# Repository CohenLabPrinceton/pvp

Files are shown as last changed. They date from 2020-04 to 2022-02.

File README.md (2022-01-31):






# The People's Ventilator Project

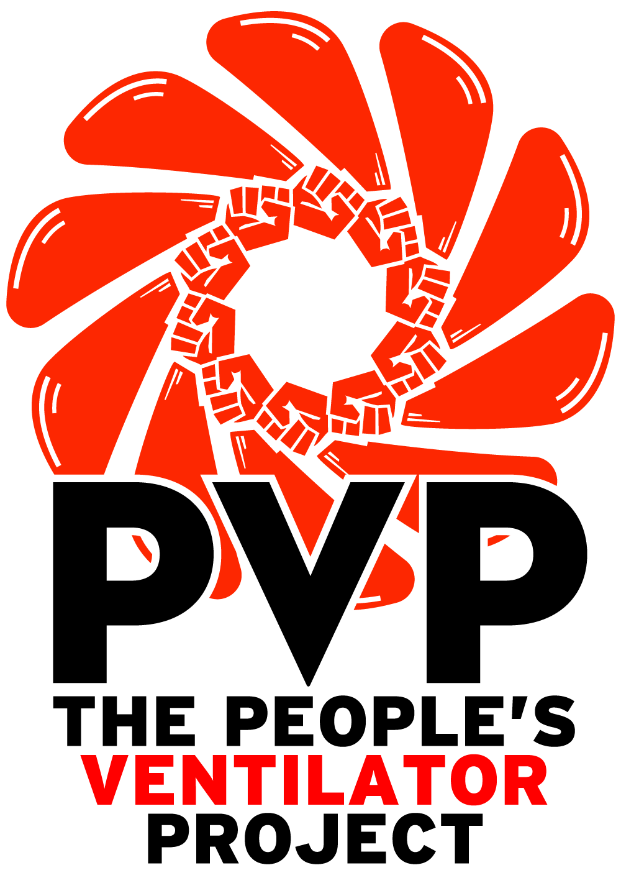
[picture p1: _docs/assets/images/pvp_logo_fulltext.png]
PVP Logo


All information is in the documentation:
https://pvp.readthedocs.io/

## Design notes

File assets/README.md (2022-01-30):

# Content of assets
This folder contains all technical drawings for PVP1, the drawings for parts to be 3D-printed, and printed circuit boards.
In addition, to aid discoverability, we have generated a standardized Open Know How Manifest (OKH-manifest): [`okh-manifest.yml`](okh-manifest.yml). This follows the Open Know-How Manifest Specification Version 1.0. Finally, the file `PVP1 Assembly Instructions.pdf` contains detailed step-by-step assembly instructions.
The following folders exist:

# cad
Contains a 3D-printable PEEP valve, as single-use PEEP valves can be subject to supply chain limitations. 

# DXFs
Contains drawings for laser cutting of the chassis.

# PCBS
This folder contains all of the electrical design files for our custom PCBs. 

# SOLIDWORKS
This folder contains CAD drawings of PVP1, more specifically:
1. Technical drawings of the PVP1 Mk3, in Solidworks. This is the device documented in the article, and featured in the detailed assembly instructions. This final version of PVP1 removed non-critical components, such as the humidifier and Gauges, and introduced more standardized parts.
1. The previous version of the device, Mk2, using few standardized components, and featuring a humidifier. Notice the `CPAP_BIPAP_HEATER_HUMIDIFIER_ASSY`.
1. Mk1, the first version of PVP1. This served as an early sketch about what to include in the design

# STLs
This folder contains all of our 3D printed components/fixtures that are not included in our Bill-of-Materials.

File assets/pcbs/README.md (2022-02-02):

# Content of pcbs
This folder contains PCB design files for the PVP1. There are two boards: one for the Actuators and one for the Sensors. They connect to the the Raspberry Pi 4 via 40-pin stackable headers. Uploaded as KiCad project files except where noted.

# Actuator Board (actuators-rev2)
	- Interfaces the Raspberry Pi to the inspiratory and expiratory valves through an array of solenoid drivers (ULN2003A Darlington transistor array)
	- Revision history:
		- rev2 (6/14/2020): Present version. Removed one screw terminal and the adjustable headers. Four of the darlington pairs are tied together to drive the expiratory valve, and three are tied together to drive the proportional valve. These connections are now permanent traces on the PCB.
		- rev1 (5/13/2020): Initial version. Three screw terminals intended to connect to valves. Included extra jumpers J4, J8, J9, and J10 designed to tie together Darlington pairs for felxibility if more current was needed to drive a particular valve.
		
# Sensor Board (pressure-rev2)
	- Interfaces four analog output sensors with the Raspberry Pi via I^2C commands to a 12-bit 4-channel ADC (Adafruit ADS1015)
	- Revision history:
		- rev2 (6/14/2020): Present version. Added a third auxiliary pressure sensor, and revised analog front-end for oxygen sensor. Added a TL7660 charge pump to provide a dual-sided supply to the INA126 instrumentation amplifier. Connections for I2C resistors removed.
		- rev1 (4/27/2020): Initial version. Shared as Gerber production files. Connections included for two pressure sensors, oxygen sensor, and flow sensor.

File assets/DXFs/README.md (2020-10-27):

This folder contains the .DXF files for the HDPE side panels, primarily for laser cutting applications. 

Produce two copies of the "SIDE_IP_PANEL", and one of each of the rest!

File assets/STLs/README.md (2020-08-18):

This folder contains the STL files for 3D printed adapters and brackets.

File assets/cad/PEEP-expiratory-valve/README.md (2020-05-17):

This folder contains CAD files (including Solidworks assembly and part files, STLs, and STEP versions) of the PEEP valve components.

This hardware design is licensed under the CERN Open Hardware Licence v1.2 (CERN, Geneva, Switzerland). Refer to the text file cern_ohl_v_1_2 or https://ohwr.org/project/licenses/wikis/cern-ohl-v1.2 for details. 

In the event that a commercial PEEP valve cannot be sourced, we provide these 3D printable components so that a user can produce a DIY PEEP version of the valve.

This part may serve either as a traditional PEEP valve in its standard configuration, or as a combined expiratory valve + PEEP valve, by tapping the hole in the cap with a 1/4" NPT tap, and applying pressure to this port. 

We 3D printed the PEEP valve using both ABS and PLA, on a FlashForge and Creality Ender 3 printer, respectively. 

If you are printing the PEEP components, we recommend the following print settings:

- Print at triple vertical shell and 4 horizontal shell. 
- Minimum 40% infill. (We printed ours at 20% in ABS and everything seals well, but higher infill is recommended with PLA).

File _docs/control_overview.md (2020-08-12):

# pvp control pseudocode
Describes the procedure to operate low-cost ventilator under pressure control

## Pressure control parameters
**Set in GUI**
- PIP: peak inhalation pressure (~20 cm H2O)
- T_insp: inspiratory time to PEEP (~0.5 sec)
- I/E: inspiratory to expiratory time ratio
- bpm: breaths per minute (15 bpm -> 1/15 sec cycle time)
- PIP_time: Target time for PIP. While lungs expand, dP/dt should be PIP/PIP_time
- flow_insp: nominal flow rate during inspiration

**Set by hardware**
- FiO2: fraction of inspired oxygen, set by blender
- max_flow: manual valve at output of blender
- PEEP: positive end-expiratory pressure, set by manual valve

**Derived parameters**
- cycle_time: 1/bpm
- t_insp: inspiratory time, controlled by cycle_time and I/E
- t_exp: expiratory time, controlled by cycle_time and I/E

**Monitored variables**
- Tidal volume: the volume of air entering the lung, derived from flow through t_exp
- PIP: peak inspiratory pressure, set by user in software
- Mean plateau pressure: derived from pressure sensor during inspiration cycle hold (no flow)
- PEEP: positive end-expiratory pressure, set by manual valve

**Alarms**
- Oxygen out of range
- High pressure (tube/airway occlusion)
- Low-pressure (disconnect)
- Temperature out of range 
- Low voltage alarm (if using battery power)
- Tidal volume (expiratory) out of range

## Hardware
**Sensors**
- O2 fraction, in inspiratory path
- Pressure, just before wye to endotrachial tube
- Flow, on expiratory path
- Temperature
- Humidity?

**Actuators**
- Inspiratory valve
    - Proportional or on/off
    - Must maintain low flow during expiratory cycle to maintain PEEP
- Expiratory valve
    - On/off in conjunction with PEEP valve probably OK

## Pressure control loop
1. Begin inhalation
    - v1 Triggered by program every 1/bpm sec
    - v2 triggered by momentary drop in pressure when patient initiates inhalation (technically pressure-assisted control, PAC)
    1. ExpValve.close()
    2. InspValve.set(flow_insp)
2. While PSensor.read() < PIP
    1. Monitor d(PSensor.read())/dt
    2. Adjust flow rate for desired slope with controller
4. Cut flow and hold for t_insp
    1. InspValve.close()
    2. Monitor PSensor.read() and average across this time interval to report mean plateau pressure
5. Begin exhalation and hold for t_exp
    1. InspValve.set(PEEP_flow_rate) (alt: switch to parallel tube with continuous flow)
    2. ExpValve.open()
    3. integrate(FSensor.read()) for t_exhalation to determine V_tidal
6. Repeat from step 1.

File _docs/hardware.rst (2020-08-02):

Hardware
=========

Mechanical Diagram
----------------

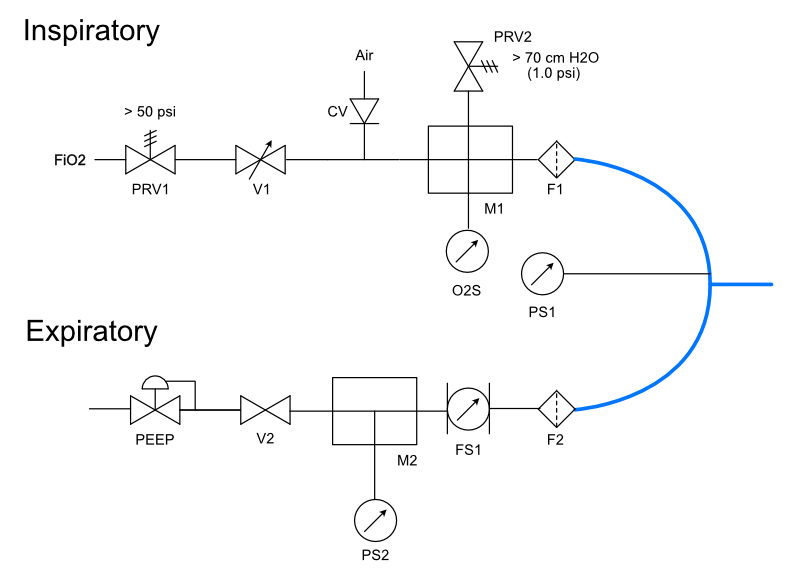
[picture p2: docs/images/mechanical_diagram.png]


    Schematic diagram of main mechanical components

.. toctree::
   :maxdepth: 4
   :caption: Hardware:

   Flow Actuators <hardware.actuators>
   Sensors <hardware.sensors>
   Safety Components <hardware.safety>
   Tubing and adapters <hardware.tubing>
   
Flow actuators
-------------------    
- Actuator PCB/overview (link to PCB with BoM, schematic, layout, etc.)    
- Proportional solenoid valve (V1) (link to doc with crit specs, driving circuit, part spec, datasheet, alternatives, etc.)
- Expiratory valve (V2) (link to doc with crit specs, driving circuit, part spec, datasheet, etc.)
    
Sensors
-------------------
- Sensor PCB/overview (link to PCB with BoM, schematic, layout, etc.)
- Oxygen sensor (O2S) (link to doc with crit specs, interface circuit, part spec, datasheet, alternatives, etc.)
- Proximal pressure sensor (PS1)
- Expiratory pressure sensor (PS2)
- Expiratory flow sensor (FS1)

Safety Components
-------------------
- 50 psi, high pressure relief valve (PRV1)
- Safety check valve (CV)
- 70 cmH2O patient-side pressure relief valve (PRV2)
- Filters (F1, F2)
- PEEP valve (PEEP) (include the design bifurcation in this module description)

Tubing and Adapters
-------------------
- Manifold 1
- Manifold 2
- Mounting Bracket 1... etc.

Bill of Materials (need to think about what goes in this table, probably separate BoMs into tables by category, but here's a sample table)
-------------------

.. list-table:: 
   :widths: 15 50 50 50
   :header-rows: 1

   * - Ref
     - Name
     - Part
     - Description
   * - V1
     - Inspiratory on/off valve
     - red hat process valve
     - completely cut off flow if required
   * - PRV1
     - High pressure relief valve
     - Sets to 50 psi
     - regulates upstream pressure to 50 psi
   * - CV
     - Inspiratory check valve
     - valve stat here
     - In case of emergency power loss, allows patient to continue taking breaths from air
   * - PRV2
     - Maximum pressure valve
     - ...
     - Sets absolute maximum pressure at patient side to 53 cm H2O
   * - F1/F2
     - Filters
     - HEPA filters?
     - Keeps the system's sensors from becoming contaminated
   * - O2S
     - Oxygen sensor
     - Sensiron ...
     - Checks FiO2 level
   * - PS1/PS2
     - Pressure sensors
     - mini4v
     - Uses gas takeoffs to measure pressure at each desired point
   * - FS1
     - Flow sensor
     - Sensiron flow sensor
     - Measures expiratory flow to calculate tidal volume
   * - M1/M2
     - Manifolds
     - 3D printed parts
     - Hubs to connect multiple components in one place
   * - V3
     - Expiratory on/off valve
     - Festo Electrical Air Directional Control Valve, 3/2 flow, Normally Closed, 8 mm Push-to-Connect
     - Opens to initiation the expiratory cycle
   * - PEEP
     - PEEP backpressure valve
     - PEEP valve
     - Sets PEEP on expiratory cycle!

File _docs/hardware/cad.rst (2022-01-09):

CAD
====

3D Printed Parts
------------------------

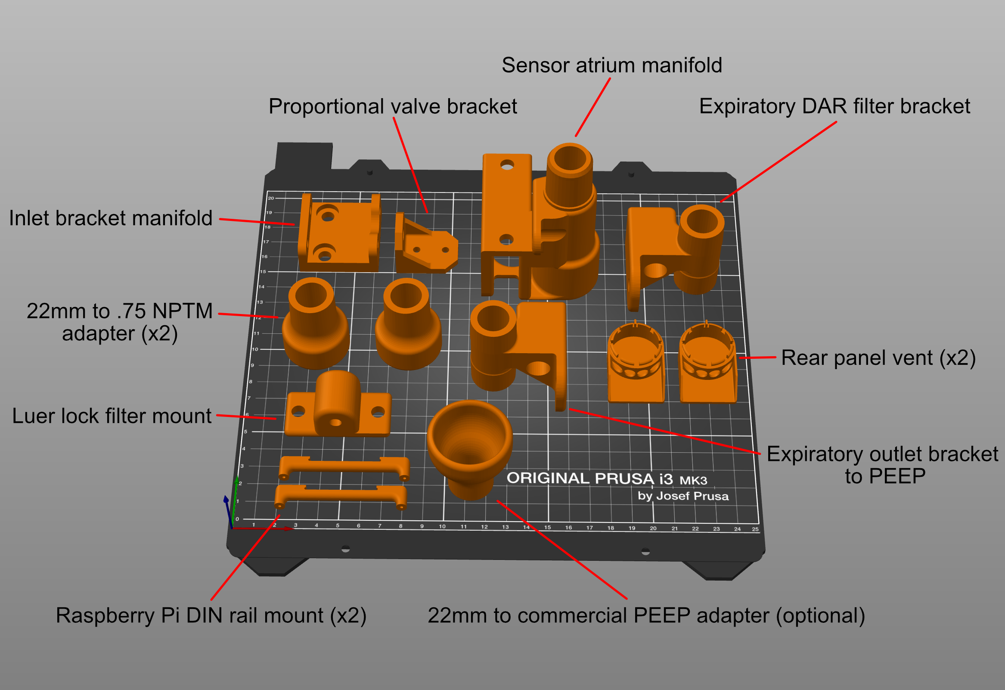
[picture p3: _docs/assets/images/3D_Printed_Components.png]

    
    Sample Prusa project with 3D printed components

Individual 3D printed parts may be downloaded here: 

* :download:`Inlet manifold bracket - [.stl] </assets/STLs/INLET_AIR_MAINFOLD_BRACKET_REV_2.STL>`
* :download:`Proportional valve bracket - [.stl] </assets/STLs/INSPIRATORY_PROPORTIONAL_VALVE_BRACKET.STL>`
* :download:`Sensor atrium manifold - [.stl] </assets/STLs/SENSOR_ATRIUM_V4.STL>`
* :download:`Expiratory DAR filter bracket - [.stl] </assets/STLs/EXPIRATORY_DAR_FILTER_BRACKET.STL>`
* :download:`22mm to 0.75 NPTM adapter (x2) - [.stl] </assets/STLs/22MM_OD_TO_0.75_NPTM_ADAPTER.STL>`
* :download:`Expiratory outlet bracket to PEEP - [.stl] </assets/STLs/EXPIRATORY_OUTLET_BRACKET_TO_PEEP_DVC.STL>`
* :download:`Luer lock filter mount - [.stl] </assets/STLs/LUER_LOCK_FILTER_MOUNT_V1.STL>`
* :download:`Raspberry Pi DIN rail mount (x2) - [.stl] </assets/STLs/RASP_PI_DIN_RAIL_MOUNT_v3.STL>`
* :download:`Rear panel vent (x2) - [.stl] </assets/STLs/IP_PANEL_VENT.STL>`
* :download:`22mm to commercial PEEP adapter - [.stl] </assets/STLs/22MM_OD_TO_COMMERCIAL_PEEP_ADAPTER.STL>`

Optional RPi DIN rail mount alternative, if your printer cannot handle the feature resolution on the original DIN rail mount: 

* :download:`ALTERNATIVE Raspberry Pi DIN rail mount (x2) - [.stl] <../assets/STLs/Alternative_Raspberry_Pi_DIN_Rail_Clip.stl>`

Download all parts:

* :download:`All components - [.zip] <../assets/STLs/All_STLs.zip>`

Printing tips: Be sure to maintain high infill for airway components: ideally, use 4 wall-layers (vertical layers), minimum 40% infill, and 4 layers on both the top and bottom. Parts should be leak-tested prior to installation, for instance, with a stopper and water bath. Most of our test prints were performed using PLA, and without any supports or rafts, since these are challenging to remove later. Supports should not be necessary provided the parts are oriented mindfully on the build plate. Also, try to keep cylindrical components oriented vertically (so that the circle is traced on the build plate); this will improve circularity of the chamber. 

For PRUSA users, we provide an example project, demonstrating part orientation:

* :download:`Sample Prusa project - [.3mf] <../assets/STLs/All_PVP1_Components.3mf>`

Enclosure
------------------------

The side, top, and bottom panels are made out of 1/16" HPDE sheeting. Laser cut, or cut by hand, two of the "SIDE_IP_PANEL", and one of each of the rest! We use a perforated HPDE for the bottom panel only; the rest are solid HPDE. 

* :download:`Bottom panel (perforated) - [.dxf] <../assets/DXFs/BOTTOM_PERFORATED_PANEL.DXF>`
* :download:`Front panel - [.dxf] <../assets/DXFs/FRONT_IP_PANEL_V1.DXF>`
* :download:`Rear panel - [.dxf] <../assets/DXFs/REAR_IP_PANEL_V1.DXF>`
* :download:`Side panel (x2) - [.dxf] <../assets/DXFs/SIDE_IP_PANEL.DXF>`
* :download:`Top panel - [.dxf] <../assets/DXFs/TOP_IP_PANEL.DXF>`

Download all .DXF files: 

* :download:`All DXF files - [.zip] <../assets/DXFs/All_DXFs.zip>`

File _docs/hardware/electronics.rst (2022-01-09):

Electronics
=============

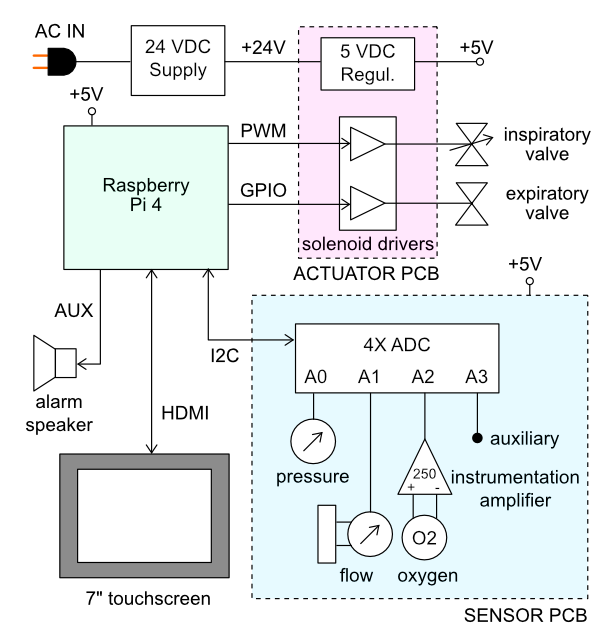
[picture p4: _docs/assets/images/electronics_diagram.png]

    
    PVP block diagram for main electrical components

The PVP is coordinated by a Raspberry Pi 4 board, which runs the graphical user interface, administers the alarm system, monitors sensor values, and sends actuation commands to the valves.
The core electrical system consists of two modular PCB 'hats', a sensor PCB and an actuator PCB, that stack onto the Raspberry Pi via 40-pin stackable headers.
The modularity of this system enables individual boards to be revised or modified to adapt to component substitutions if required.

We outsourced our PCB fabrication to Advanced Circuits, based out of Aurora, CO (for $33 each): https://www.4pcb.com/pcb-prototype-2-4-layer-boards-specials.html
If you would like to do the same, you can send them the Gerber .zip files we have provided directly.

Power and I/O
----------------
The main power to the systems is supplied by a DIN rail-mounted 150W 24V supply, which drives the inspiratory valve (4W) and expiratory valves (13W). This voltage is converted to 5V by a switched mode PCB-mounted regulated to power the Raspberry Pi and sensors.
This power is transmitted across the PCBs through the stacked headers when required.

.. csv-table:: Power and I/O bill of materials
   :file: /assets/csv/powerio_bom.csv
   :widths: 40,60
   :header-rows: 1

Sensor PCB
----------------
The sensor board interfaces four analog output sensors with the Raspberry Pi via I2C commands to a 12-bit 4-channel ADC (Adafruit ADS1015).

1. an airway pressure sensor (Amphenol 1 PSI-D-4V-MINI)
2. a differential pressure sensor (Amphenol 5 INCH-D2-P4V-MINI) to report the expiratory flow rate through a D-Lite spirometer
3. an oxygen sensor (Sensiron SS-12A) whose 13 mV differential output signal is amplified 250-fold by an instrumentation amplifier (Texas Instruments INA126)
4. a fourth auxiliary slot for an additional analog output sensor (unused)

A set of additional header pins allows for digital output sensors (such as the Sensiron SFM3300 flow sensor) to be interfaced with the Pi directly via I2C if desired. 

* :download:`Sensor PCB - [KiCad project .zip] <../assets/pcbs/pressure-rev2.zip>`

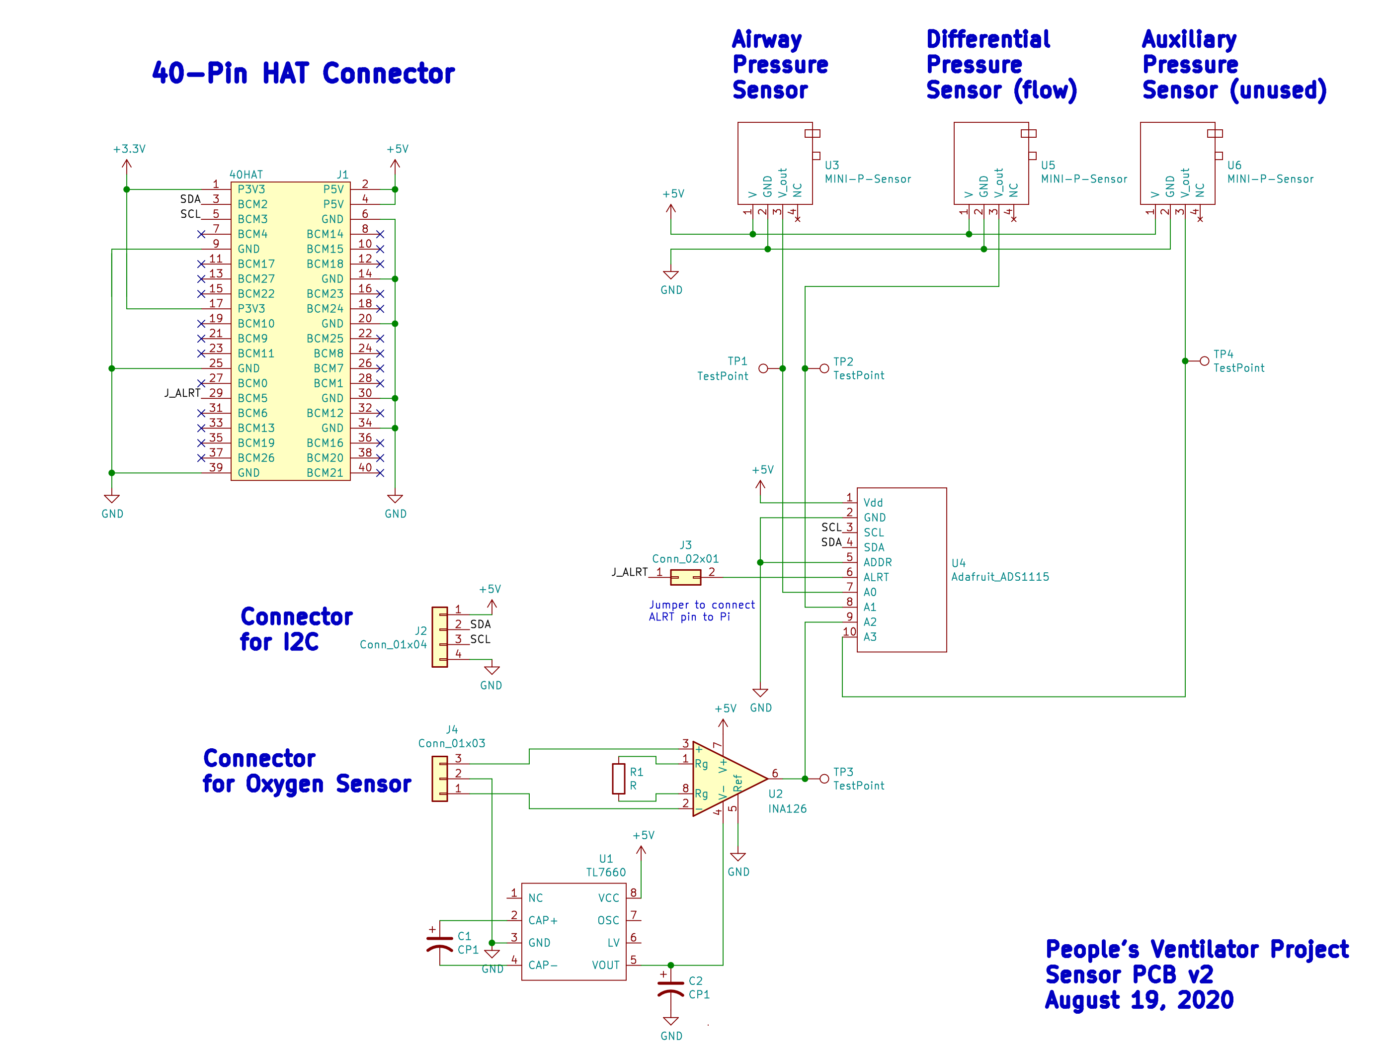
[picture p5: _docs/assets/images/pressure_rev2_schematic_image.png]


    Sensor PCB schematic
	
.. csv-table:: Sensor PCB bill of materials
   :file: /assets/csv/sensor_pcb_bom.csv
   :widths: 10,30,60
   :header-rows: 1

Actuator PCB
----------------
The purpose of the actuator board is twofold:

1. regulate the 24V power supply to 5V (CUI Inc PDQE15-Q24-S5-D DC-DC converter)
2. interface the Raspberry Pi with the inspiratory and expiratory valves through an array of solenoid drivers (ULN2003A Darlington transistor array)

* :download:`Actuator PCB - [KiCad project .zip] <../assets/pcbs/actuators-rev2.zip>`

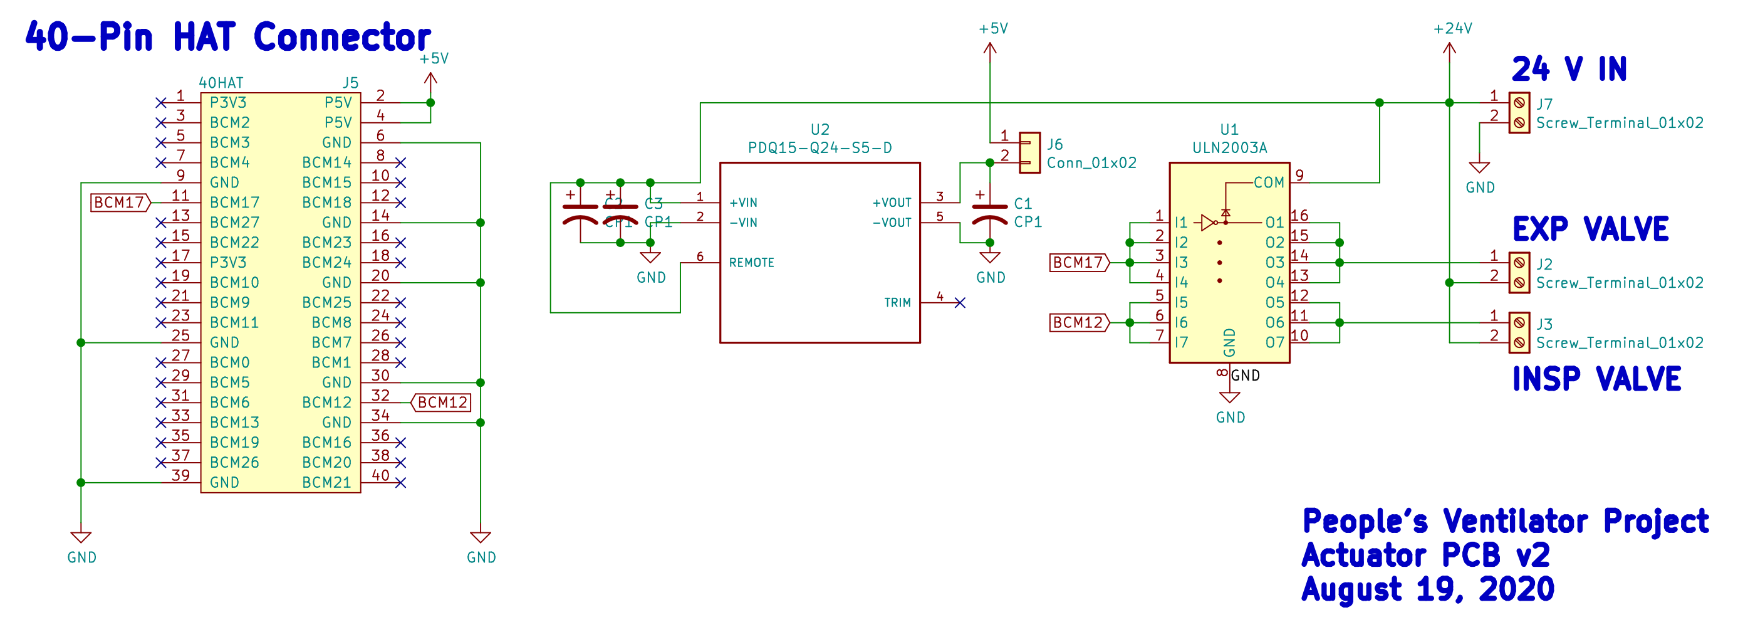
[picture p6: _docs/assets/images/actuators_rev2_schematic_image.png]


    Actuator PCB schematic

.. csv-table:: Actuator PCB bill of materials
   :file: /assets/csv/actuator_pcb_bom.csv
   :widths: 10,30,60
   :header-rows: 1

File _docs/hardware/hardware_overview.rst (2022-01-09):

Hardware Overview
==================

Schematic diagram of main mechanical components

The PVP components were selected to enable a **minimalistic and relatively low-cost ventilator design**, to avoid supply chain limitations, and to facilitate rapid and easy assembly. Most parts in the PVP are not medical-specific devices, and those that are specialized components are readily available and standardized across ventilator platforms, such as standard respiratory circuits and HEPA filters. We provide complete assembly of the PVP, including 3D-printable components, as well as justifications for selecting all actuators and sensors, as guidance to those who cannot source an exact match to components used in the Bill of Materials.


    
    PVP hardware schematic

.. raw:: html

    <div class="software-summary">
	    <a href="components.html"><h2>Components</h2></a> <p>Justifcation behind the components actuators and sensors selected for the PVP.</p>
		<a href="assembly.html"><h2>Assembly</h2></a> <p>Solidworks model of the system assembly, description of enclosure, and models for 3D printed components.</p>
        <a href="electronics.html"><h2>Electronics</h2></a> <p>Modular PCBs that interface the PVP actuators and sensors with the Raspberry Pi.</p>
		<a href="bom.html"><h2>Bill of Materials</h2></a> <p>Itemized PVP parts list.</p>
	</div>

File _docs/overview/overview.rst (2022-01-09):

System Overview
=================

The **People's Ventilator Project (PVP)** is an open-source, low-cost pressure-control ventilator designed for minimal reliance on specialized medical parts to better adapt to supply chain shortages.

.. raw:: html

    <video width="100%" autoplay loop>
      <source src="/images/ventilator_rotate.mp4" type="video/mp4">
    Video of a rotating ventilator
    </video>

Hardware
--------

.. raw:: html
    :file: /assets/images/Schematic_v2.svg

The device components were selected to enable a **minimalistic and relatively low-cost ventilator design, 
to avoid supply chain limitations, and to facilitate rapid and easy assembly**. 
Most parts in the PVP are not medical-specific devices, and those that are specialized components 
are readily available and standardized across ventilator platforms, such as standard respiratory 
circuits and HEPA filters. We provide complete assembly of the PVP, 
including 3D-printable components, as well as justifications for selecting all actuators and sensors,
as guidance to those who cannot source an exact match to components used in the Bill of Materials.

PVP Hardware
_____________

.. raw:: html

    <div class="software-summary">
	    <a href="../hardware/components.html"><h2>Components</h2></a> <p>Justifcation behind the components actuators and sensors selected for the PVP.</p>
		<a href="../hardware/assembly.html"><h2>Assembly</h2></a> <p>Solidworks model of the system assembly, description of enclosure, and models for 3D printed components.</p>
        <a href="../hardware/electronics.html"><h2>Electronics</h2></a> <p>Modular PCBs that interface the PVP actuators and sensors with the Raspberry Pi.</p>
		<a href="../hardware/bom.html"><h2>Bill of Materials</h2></a> <p>Itemized PVP parts list.</p>
	</div>

Software
--------

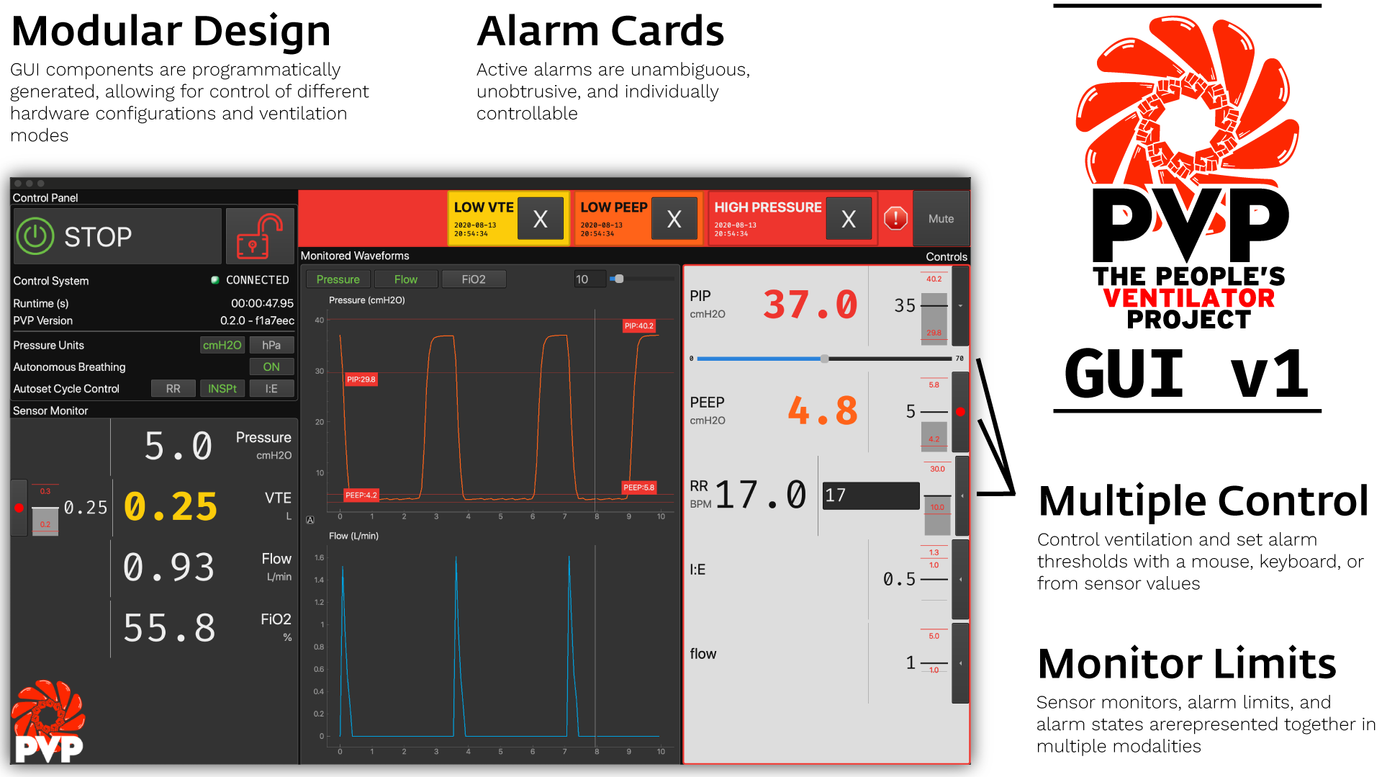
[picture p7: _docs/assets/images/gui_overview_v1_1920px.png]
Gui Overview - modular design, alarm cards, multiple modalities of input, alarm limits represented consistently across ui


PVP's software was developed to bring the philosophy of free and open-source software to medical devices. PVP is not only
open from top to bottom, but we have developed it as a framework for **an adaptable, general-purpose, communally-developed ventilator.**

PVP's ventilation control system is fast, robust, and **written entirely in high-level Python** (3.7) -- without the development
and inspection bottlenecks of split computer/microprocessor systems that require users to read and write low-level hardware firmware.

All of PVP's components are **modularly designed**, allowing them to be reconfigured and expanded for new ventilation modes and
hardware configurations.

We provide complete **API-level documentation** and an **automated testing suite**
to give everyone the freedom to inspect, understand, and expand PVP's software framework.

PVP Modules
____________

.. raw:: html

    <div class="software-summary">
        <a href="../software/gui/index.html"><h2>GUI</h2></a> <p>A modular GUI with intuitive controls and a clear alarm system that can be configured to control any parameter or display values from any sensor.</p>
        <a href="../software/controller.html"><h2>Controller</h2></a> <p>A PID Controller to produce a pressure-controlled waveform, while monitoring for possible alarm states.</p>
        <a href="../software/io.html"><h2>IO</h2></a> <p>A hardware abstraction layer powered by <a href="http://abyz.me.uk/rpi/pigpio/">pigpio</a> that can read/write at [x Hz]</p>
        <a href="../software/alarm.html"><h2>Alarm</h2></a> <p>Define complex and responsive alarm triggering criteria with human-readable Alarm Rules</p>
        <a href="../software/common.html"><h2>Common</h2><a> <p>Modules that provide the API between the GUI and controller, user preferences, and other utilities</p>
    </div>

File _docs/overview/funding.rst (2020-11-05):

Funding and Support
===================

Funding and lab space for this project was provided by Princeton University in direct response to the COVID-19 pandemic. 
Note: See Disclaimer for further details. 

We wish to thank the Trevor Day School of NYC (https://www.trevor.org) for their kind loan of multiple 3D printers, which greatly contributed to the rapid prototyping efforts of the team. Additional thanks are in order to recognize the indeterminate length of the loan (...no really, thanks for not asking for them back yet). 

We also wish to thank Nick and Alex Winnard of the Berkshire Laser Co. in Pittsfield, MA (https://berkshirelaserco.com/) for generously donating their laser cutting and engraving services. We are grateful for their skills and expertise in creating the gorgeous acrylic enclosure, as displayed on our prototype device, and guidance improving the enclosure documentation.

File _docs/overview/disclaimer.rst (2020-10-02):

Medical Disclaimer
==================

PVP1 is not a regulated or clinically validated medical device. We have not yet performed testing for safety or efficacy on living organisms. All material described herein should be used at your own risk and do not represent a medical recommendation. PVP1 is currently recommended only for research purposes.

This website is not connected to, endorsed by, or representative of the view of Princeton University. Neither the authors nor Princeton University assume any liability or responsibility for any consequences, damages, or loss caused or alleged to be caused directly or indirectly for any action or inaction taken based on or made in reliance on the information or material discussed herein or linked to from this website.

PVP1 is under continuous development and the information here may not be up to date, nor is any guarantee made as such. Neither the authors nor Princeton University are liable for  any damage or loss related to the accuracy, completeness or timeliness of any information described or linked to from this website.

By continuing to watch or read this, you are acknowledging and accepting this disclaimer.

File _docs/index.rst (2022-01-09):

.. title:: The People's Ventilator Project

.. raw:: html

   <div class="header-img" >
      People's Ventilator Project logo
      <div>
         <h1>A fully-open</h1>
         <h1>Supply-chain resilient</h1>
         <h1>pressure-control ventilator</h1>
         <h1 style="color: #fd2701;">for the people</h1>
		 <h3>A project funded and supported by Princeton University</h3>
      </div>
   </div>

The global COVID-19 pandemic has highlighted the need for a low-cost, rapidly-deployable ventilator, for the current as well as future respiratory virus outbreaks.
While safe and robust ventilation technology exists in the commercial sector, the small number of capable suppliers cannot meet the severe demands for ventilators during a pandemic.
Moreover, the specialized, proprietary equipment developed by medical device manufacturers is expensive and inaccessible in low-resource areas.

The **People's Ventilator Project (PVP)** is an open-source, low-cost pressure-control ventilator designed for minimal reliance on specialized medical parts to better adapt to supply chain shortages.
The **PVP** largely follows established design conventions, most importantly active and computer-controlled inhalation, together with passive exhalation.
It supports pressure-controlled ventilation, combined with standard-features like autonomous breath detection, and the suite of FDA required alarms.

`See our medRxiv preprint here!
<https://www.medrxiv.org/content/10.1101/2020.10.02.20206037v1>`_

.. raw:: html

    <video width="100%" autoplay loop>
      <source src="images/ventilator_rotate.mp4" type="video/mp4">
    Video of a rotating ventilator
    </video>

=======

Hardware
=========

PVP is a pressure-controlled ventilator that uses a minimal set of inexpensive, off-the-self hardware components.
An inexpensive proportional valve controls inspiratory flow, and a relay valve controls expiratory flow.
A gauge pressure sensor monitors airway pressure, and an inexpensive D-lite spirometer used in conjunction with a differential pressure sensor monitors expiratory flow.

.. raw:: html

    <object type="image/svg+xml" data="assets/images/Schematic_v2.svg">
    Hardware schematic for People's Ventilator Project
    </object>

PVP's components are coordinated by a Raspberry Pi 4 board, which runs the graphical user interface, administers the alarm system, monitors sensor values, and sends actuation commands to the valves.
The core electrical system consists of two modular board 'hats', a sensor board and an actuator board, that stack onto the Raspberry Pi via 40-pin stackable headers.
The modularity of this system enables individual boards to be revised or modified to substitute components in the case of part scarcity.

Software
========

Gui Overview - modular design, alarm cards, multiple modalities of input, alarm limits represented consistently across ui

PVP's software was developed to bring the philosophy of free and open-source software to medical devices. PVP is not only
open from top to bottom, but we have developed it as a framework for **an adaptable, general-purpose, communally-developed ventilator.**

PVP's ventilation control system is fast, robust, and **written entirely in high-level Python** (3.7) -- without the development
and inspection bottlenecks of split computer/microprocessor systems that require users to read and write low-level hardware firmware.

All of PVP's components are **modularly designed**, allowing them to be reconfigured and expanded for new ventilation modes and
hardware configurations.

We provide complete **API-level documentation** and an **automated testing suite**
to give everyone the freedom to inspect, understand, and expand PVP's software framework.

PVP Modules
------------

.. raw:: html

    <div class="software-summary">
        <a href="gui.html"><h2>GUI</h2></a> <p>A modular GUI with intuitive controls and a clear alarm system that can be configured to control any parameter or display values from any sensor.</p>
        <a href="controller.html"><h2>Controller</h2></a> <p>A PID Controller to produce a pressure-controlled waveform, while monitoring for possible alarm states.</p>
        <a href="io.html"><h2>IO</h2></a> <p>A hardware abstraction layer powered by <a href="http://abyz.me.uk/rpi/pigpio/">pigpio</a> with socket pipeline latency of 0.9 ms.</p>
        <a href="alarm.html"><h2>Alarm</h2></a> <p>Define complex and responsive alarm triggering criteria with human-readable Alarm Rules</p>
        <a href="common.html"><h2>Common</h2></a> <p>Modules that provide the API between the GUI and controller, user preferences, and other utilities</p>
    </div>

.. toctree::
   :hidden:
   :maxdepth: 4
   :caption: Overview

   System Overview <overview/overview>
   Performance <overview/performance>
   Medical Disclaimer <overview/disclaimer>
   Funding and Support <overview/funding>

.. toctree::
   :hidden:
   :maxdepth: 4
   :caption: Hardware:

   Hardware Overview <hardware/hardware_overview>
   Components <hardware/components>
   Assembly <hardware/assembly>
   Electronics <hardware/electronics>
   Bill of Materials <hardware/bom>
   CAD <hardware/cad>

.. toctree::
   :hidden:
   :maxdepth: 4
   :caption: Software:

   Software Overview <software/software_overview>
   GUI <software/gui/index>
   Controller <software/controller>
   Common <software/common/index>
   I/O <software/io>
   Alarm <software/alarm/index>
   Coordinator <software/coordinator>

.. toctree::
   :hidden:
   :maxdepth: 4
   :caption: Meta:

   Index <meta_index>
   
Medical Disclaimer
===================
PVP1 is not a regulated or clinically validated medical device. We have not yet performed testing for safety or efficacy on living organisms. All material described herein should be used at your own risk and do not represent a medical recommendation. PVP1 is currently recommended only for research purposes.

This website is not connected to, endorsed by, or representative of the view of Princeton University. Neither the authors nor Princeton University assume any liability or responsibility for any consequences, damages, or loss caused or alleged to be caused directly or indirectly for any action or inaction taken based on or made in reliance on the information or material discussed herein or linked to from this website.

PVP1 is under continuous development and the information here may not be up to date, nor is any guarantee made as such. Neither the authors nor Princeton University are liable for  any damage or loss related to the accuracy, completeness or timeliness of any information described or linked to from this website.

By continuing to watch or read this, you are acknowledging and accepting this disclaimer.

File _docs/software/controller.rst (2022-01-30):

.. _controller_overview:

Controller
=================

Purpose of the Controller
---------------------------

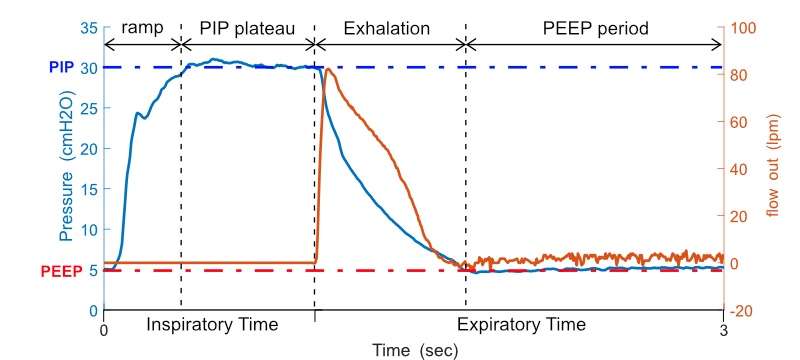
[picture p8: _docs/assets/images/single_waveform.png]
Raw data for a single breath; blue is pressure and orange is flow-out.


Shown above is a typical respiratory waveform (without averaging) as produced with PVP1. Blue is the recorded pressure, orange is the flow out of the system. Note that airflow (and also oxygen concentration) are only measured during expiration, so that the main control-loop during inspiration runs as fast as possible, and is not slowed down by communication delays. Pressure is recorded continuously. Empirically, the Raspberry pi allowed for the primary control loop to run at speeds of ~5ms per loop, which was considerably faster than all hardware delays (i.e. the time it takes for a mechanical, physical valve to open or close; see main manuscript).

The purpose of the controller is to produce a breath waveform, as the one shown above. More specifically, it's job is to reach a certain target-pressure (PIP), and to hold that pressure for a certain amount of time. These numbers are provided by the user via thee UI. Exhalation is passive, and PEEP pressure is mechanically controlled with a spring-valve.

Conceptually, the controller is written as a hybrid system of state and PID control. During inspiration, it actively controls pressure with a simple `PID controller <https://en.wikipedia.org/wiki/PID_controller>`_. That means that during inspiration, it measures the deviation of the pressure-is-vale from the pressure-target-value, and depending an that distance (and its integral and derivative), it adjusts the opening of the inspiratory valve. Expiration was then instantiated by closing the inspiratory, and opening the expiratory valve to passively release PIP pressure as fast as possible. After reaching PEEP, the controller opens the inspiratory valve slightly to sustain a small flow during PEEP, using the aforementioned manually operated PEEP-valve. We found, empirically, that a combination of proportional and integral term worked best across different physical lung settings.

The controller was also built to allow the user to adjust flow through the system. This is done by a linear correction of the proportional-term. With this adjustment, the user can  manipulate the rise-time of the pressure waveform.

In addition to this core function, the controller module continuously monitors for autonomous breaths, high airway pressure, and general system status. Autonomous breathing was detected by transient pressure drops below PEEP. A detected breath triggered a new breath cycle. High airway pressure is defined as exceeding a certain pressure for a certain time (as to not be triggered by a cough). This event triggered an alarm, and  an immediate release of air to drop to a safe pressure and not to exceed PIP. Both of these functionalities are fast, and respond, at the latest, within few hundred milliseconds. The controller also assesses whether numerical values and sensor readings are reasonable, and changing over time. If this is not the case, it raises an technical alarm. All alarms are collected and maintained by an intelligent alarm manager, that provides the UI with the alarms to display in order of their importance. 

The final functionality of the control module is the estimation of VTE (VTE stands for exhaled tidal volume), which is thee volume of air that made it in- and out of the lung. We estimate this number by integrating the expiratory flow during expiration, and subtracting the baseline flow used to sustain PEEP (details in the accompanying manuscript):

Architecture of the Controller
--------------------------------

In terms of software components, the Controller consists of one main :class:`~.pvp.controller` class, that is instantiated in its own thread. This object receives sensor-data from HAL, and computes control parameters, to change the mechanical position of valves. The Controller also receives ventilation control parameters (see :meth:`~.PVP_Gui.set_control`). All exchanged variables are mutex'd.

The Controller also feeds the :class:`.Logger` a continuous stream of :class:`.SensorValues` objects so as to store high-temporal resolution data, including the control signals.

The main **control loop** is :meth:`.pvp.controller._start_mainloop()` which queries the Hardware for new variables, and performs a PID update using `.pvp.controller._PID_update()`.

The Controller is **configured** by the :mod:`~.common.values` module, 

The Controller can be launched alone, but was not intended to be launched alone. The alarm functionality requires the UI.

.. automodule:: pvp.controller.control_module
   :members:
   :show-inheritance:

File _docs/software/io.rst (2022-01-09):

pvp.io package
===============

.. automodule:: pvp.io
   :members:
   :undoc-members:
   :show-inheritance:

pvp.io.hal module
------------------

.. automodule:: pvp.io.hal
   :members:
   :undoc-members:
   :show-inheritance:

devices
---------

.. automodule:: pvp.io.devices
   :members:
   :undoc-members:
   :show-inheritance:

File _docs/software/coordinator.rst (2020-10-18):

.. _coordinator_overview:

coordinator module
========================

The coordinator provides an interface between the process threads, and facilitates inter-process communication. It is a wrapper around xml-rpc, which allowed us to use defined data-structures such as :class:`.SensorValues`.

Submodules
----------

coordinator
-----------------------------------

.. automodule:: pvp.coordinator.coordinator
   :members:
   :undoc-members:
   :show-inheritance:

ipc
---------------------------

.. automodule:: pvp.coordinator.rpc
   :members:
   :undoc-members:
   :show-inheritance:

process\_manager
----------------------------------------

.. automodule:: pvp.coordinator.process_manager
   :members:
   :undoc-members:
   :show-inheritance:

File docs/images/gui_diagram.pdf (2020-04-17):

Vent GUI

Status_Bar

monitor

controls

plots

gui.defaults

(populates values
and sets default
values & ranges)

Power_Button

HeartBeat

Message_Display

Alarm_Manager

gui.styles

(stylesheets for
all widgets)
menus | load/save
| display_logs
| test_mode?

~/.vent_state.json

Monitor_Value (1)

Messenger

Monitor_Value(2)

Control (1)

Control (2)

Plot (1)

Plot (2)

Signals
Slots

Widgets

update_value

update_message

update_value

getSensors
getAlarms
setControls

Socket Connection
to Control Process

limits_changed

Communication
Parenthood

value_changed

beatHeart

heartBeat

beatHeart

heartBeat

toggleStart

start_stop

message_cleared

process_alarm

alarm

alarm

If last open was < reset_time

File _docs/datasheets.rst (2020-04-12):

Datasheets & Manuals
========================

Manuals
---------

* `Hamilton T1 Quick Guide`_

Other Reference Material
--------------------------

* `Hamilton UI Simulator`_

.. _Hamilton T1 Quick Guide: /hamilton-t1-quick-guide.pdf
.. _Hamilton UI Simulator: https://www.hamilton-medical.com/en_US/News/News/News-Detail~2018-12-12~Download-our-new-HAMILTON-C6-simulation-software%21~a499c16c-174c-4e6f-9c75-2f5be2972f94~.html

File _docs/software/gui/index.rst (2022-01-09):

.. _gui_overview:

GUI
======

.. toctree::
   :hidden:
   :maxdepth: 4

   PVP GUI <main>
   Widgets <widgets/index>
   Stylesheets <styles>

.. raw:: html
   :file: ../../assets/images/pvp_gui_overview_clickable.svg

The GUI is written using `PySide2 <https://wiki.qt.io/Qt_for_Python>`_ and consists of one main :class:`~.gui.main.PVP_Gui`
object that instantiates a series of :ref:`gui_widgets`. The GUI is responsible for setting ventilation control parameters
and sending them to the :mod:`~pvp.controller` (see :meth:`~.PVP_Gui.set_control`), as well as receiving and displaying sensor values (:meth:`~.ControlModuleBase.get_sensors`).

The GUI also feeds the :class:`.Alarm_Manager` :class:`.SensorValues` objects so that it can compute alarm state. The :class:`.Alarm_Manager`
reciprocally updates the GUI with :class:`.Alarm` s (:meth:`.PVP_Gui.handle_alarm`) and Alarm limits (:meth:`.PVP_Gui.limits_updated`).

The main **polling loop** of the GUI is :meth:`.PVP_Gui.update_gui` which queries the controller for new :class:`.SensorValues` and distributes
them to all listening widgets (see method documentation for more details). The rest of the GUI is event driven, usually with Qt
Signals and Slots.

The GUI is **configured** by the :mod:`~.common.values` module, in particular it creates

* :class:`~.widgets.display.Display` widgets in the left "sensor monitor" box from all :class:`~.common.values.Value` s in :data:`~.values.DISPLAY_MONITOR` ,
* :class:`~.widgets.display.Display` widgets in the right "control" box from all :class:`~.common.values.Value` s in :data:`~.values.DISPLAY_CONTROL` , and
* :class:`~.widgets.plot.Plot` widgets in the center plot box from all :class:`~.common.values.Value` s in :data:`~.values.PLOT`

The GUI is not intended to be launched alone, as it needs an active :mod:`~pvp.coordinator` to communicate with the controller process
and a few prelaunch preparations (:func:`~.gui.main.launch_gui`). PVP should be started like::

    python3 -m pvp.main

Module Overview
----------------

.. raw:: html

    <div class="software-summary">
        <a href="main.html"><h2>PVP_Gui</h2></a> <p>Main GUI Object that controls all the others!</p>
        <a href="widgets/index.html"><h2>Widgets</h2></a> <p>Widgets used by main GUI</p>
        <a href="styles.html"><h2>IO</h2></a> <p>Stylesheets used by the GUI</p>
    </div>

Screenshot
----------

Gui Overview - modular design, alarm cards, multiple modalities of input, alarm limits represented consistently across ui

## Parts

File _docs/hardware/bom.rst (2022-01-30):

Bill of Materials
==================

The complete bill of materials is available here:
* :download:`Bill of materials - [.csv] </assets/csv/10_27_2020_bom.csv>`

The following tables are summarized versions of the CSV file above, and illustrate the approximate unit cost
(state 10/2020) of a single device, together with links to manufactures of the parts:

**GRAND TOTAL: $1,753.57**

I/O
----

.. csv-table:: PVP bill of materials
   :file: /assets/csv/10_27_2020_bom_io.csv
   :header-rows: 1

Airway
-------

.. csv-table:: PVP bill of materials
   :file: /assets/csv/10_27_2020_bom_airway.csv
   :header-rows: 1

Framing & Structural
---------------------

.. csv-table:: PVP bill of materials
   :file: /assets/csv/10_27_2020_bom_structural.csv
   :header-rows: 1

Electronics
------------

.. csv-table:: PVP bill of materials
   :file: /assets/csv/10_27_2020_bom_electronics.csv
   :header-rows: 1

Specialized Tools
------------------

.. csv-table:: PVP bill of materials
   :file: /assets/csv/10_27_2020_bom_tools.csv
   :header-rows: 1

Etc.
-----

.. csv-table:: PVP bill of materials
   :file: /assets/csv/10_27_2020_bom_etc.csv
   :header-rows: 1

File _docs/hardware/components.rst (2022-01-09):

Components
==================


    
    PVP hardware schematic

Hardware Design
-------------------

The following is a guided walk through the main hardware components that comprise the respiratory circuit,
roughly following the flow of gas from the system inlet, to the patient, then out through the expiratory valve.

**Hospital gas blender.**
At the inlet to the system, we assume the presence of a commercial-off-the-shelf (COTS) gas blender. These devices mix air from U.S. standard medical air and O2 as supplied at the hospital wall at a pressure of around 50 psig. The device outlet fitting may vary, but we assume a male O2 DISS fitting (NIST standard). In field hospitals, compressed air and O2 cylinders may be utilized in conjunction with a gas blender, or a low-cost Venturi-based gas blender. We additionally assume that the oxygen concentration of gas supplied by the blender can be manually adjusted. Users will be able to monitor the oxygen concentration level in real-time on the device GUI. 

**Fittings and 3D printed adapters.**
Standardized fittings were selected whenever possible to ease part sourcing in the event that engineers replicating the system need to swap out a component, possibly as the result of sourcing constraints within their local geographic area. Many fittings are American national pipe thread (NPT) standard, or conform to the respiratory circuit tubing standards (15mm I.D./22 mm O.D.). To reduce system complexity and sourcing requirements of specialized adapters, a number of connectors, brackets, and manifold are provided as 3D printable parts. All 3D printed components were print-tested on multiple 3D printers, including consumer-level devices produced by MakerBot, FlashForge, and Creality3D. 

**Pressure regulator.**
The fixed pressure regulator near the inlet of the system functions to step down the pressure supplied to the proportional valve to a safe and consistent set level of 50 psi. It is essential to preventing the over-pressurization of the system in the event of a pressure spike, eases the real-time control task, and ensures that downstream valves are operating within the acceptable range of flow conditions.

**Proportional valve.**
The proportional valve is the first of two actuated components in the system. It enables regulation of the gas flow to the patient via the PID control framework, described in a following section. A proportional valve upstream of the respiratory circuit enables the controller to modify the inspiratory time, and does not present wear limitations like pinch-valves and other analogous flow-control devices. The normally closed configuration was selected to prevent over-pressurization of the lungs in the event of system failure. 

**Sensors.**
The system includes an oxygen sensor for monitoring oxygen concentration of the blended gas supplied to the patient, a pressure sensor located proximally to the patient mouth along the respiratory circuit, and a spirometer, consisting of a plastic housing (D-Lite, GE Healthcare) with an attached differential pressure sensor, to measure flow. Individual sensor selection will be described in more detail in a following section. The oxygen sensor read-out is used to adjust the manual gas blender and to trigger alarm states in the event of deviations from a setpoint. The proximal location of the primary pressure sensor was selected due to the choice of a pressure-based control strategy, specifically to ensure the most accurate pressure readings with respect to the patient's lungs. Flow estimates from the single expiratory flow sensor are not directly used in the pressure-based control scheme, but enable the device to trigger appropriate alarm states in order to avoid deviations from the tidal volume of gas leaving the lungs during expiration. The device does not currently monitor gas temperature and humidity due to the use of an HME rather than a heated humidification system.

**Pressure relief.**
A critical safety component is the pressure relief valve (alternatively called the "pressure release valve", or "pressure safety valve"). The proportional valve is controlled to ensure that the pressure of the gas supplied to the patient never rises above a set maximum level. The relief valve acts as a backup safety mechanism and opens if the pressure exceeds a safe level, thereby dumping excess gas to atmosphere. Thus, the relief valve in this system is located between the proportional valve and the patient respiratory circuit. The pressure relief valve we source cracks at 1 psi (approx 70 cm H2O).

**Standard respiratory circuit.**
The breathing circuit which connects the patient to the device is a standard respiratory circuit: the flexible, corrugated plastic tubing used in commercial ICU ventilators. Because this system assumes the use of an HME/F to maintain humidity levels of gas supplied to the patient, specialized heated tubing is not required. 
 
**Anti-suffocation check valve.** 
A standard ventilator check valve (alternatively called a "one-way valve") is used as a secondary safety component in-line between the proportional valve and the patient respiratory circuit. The check valve is oriented such that air can be pulled into the system in the event of system failure, but that air cannot flow outward through the valve. A standard respiratory circuit check valve is used because it is a low-cost, readily sourced device with low cracking pressure and sufficiently high valve flow coefficient (Cv). 
 
**Bacterial filters.**
A medical-grade electrostatic filter is placed on either end of the respiratory circuit. These function as protection against contamination of device internals and surroundings by pathogens and reduces the probability of the patient developing a hospital-acquired infection. The electrostatic filter presents low resistance to flow in the airway.
 
**HME.**
A Heat and Moisture Exchanger (HME) is placed proximal to the patient. This is used to passively humidify and warm air inspired by the patient. HMEs are the standard solution in the absence of a heated humidifier. While we evaluated the use of an HME/F which integrates a bacteriological/viral filter, use of an HME/F increased flow resistance and compromised pressure control. 

**Pressure sampling filter.**
Proximal airway pressure is sampled at a pressure port near the wye adapter, and measured by a pressure sensor on the sensor PCB. To protect the sensor and internals of the ventilator, an additional 0.2 micron bacterial/viral filter is placed in-line between the proximal airway sampling port and the pressure sensor. This is also a standard approach in many commercial ventilators. 

**Expiratory solenoid.**
The expiratory solenoid is the second of two actuated components in the system. When this valve is open, air bypasses the lungs, thereby enabling the lungs to de-pressurize upon expiration. When the valve is closed, the lungs may inflate or hold a fixed pressure, according to the control applied to the proportional valve. The expiratory flow control components must be selected to have a sufficiently high valve flow coefficient (Cv) to prevent obstruction upon expiration. This valve is also selected to be normally open, to enable the patient to expire in the event of system failure. 

**Manual PEEP valve.**
The PEEP valve is a component which maintains the positive end-expiratory pressure (PEEP) of the system above atmospheric pressure to promote gas exchange to the lungs. A typical COTS PEEP valve is a spring-based relief valve which exhausts when pressure within the airway exceeds a fixed limit. This limit is manually adjusted via compression of the spring. Various low-cost alternatives to a COTS mechanical PEEP valve exist, including the use of a simple water column, in the event that PEEP valves become challenging to source. We additionally provide a 3D printable PEEP valve alternative which utilizes a thin membrane, rather than a spring, to maintain PEEP. 

Actuator Selection
---------------------

When planning actuator selection, it was necessary to consider the placement of the valves within the larger system. Initially, we anticipated sourcing a proportional valve to operate at very low pressures (0-50 cm H20) and sufficiently high flow (over 120 LPM) of gas within the airway. However, a low-pressure, high-flow regime proportional valve is far more expensive than a proportional valve which operates within high-pressure (~50 psi), high-flow regimes. Thus, we designed the device such that the proportional valve would admit gas within the high-pressure regime and regulate air flow to the patient from the inspiratory airway limb. 
Conceivably, it is possible to control the air flow to the patient with the proportional valve alone. However, we couple this actuator with a solenoid and PEEP valve to ensure robust control during PIP (peak inspiratory pressure) and PEEP hold, and to minimize the loss of O2-blended gas to the atmosphere, particularly during PIP hold.

**Proportional valve sourcing.**
Despite designing the system such that the proportional valve could be sourced for operation within a normal inlet pressure regime (approximately 50 psi), it was necessary to search for a valve with a high enough valve flow coefficient (Cv) to admit sufficient gas to the patient. We sourced an SMC PVQ31-5G-23-01N valve with stainless steel body in the normally-closed configuration. This valve has a port size of 1/8" (Rc) and has previously been used for respiratory applications. Although the manufacturer does not supply Cv estimates, we empirically determined that this valve is able to flow sufficiently for the application.

**Expiratory valve sourcing.**
When sourcing the expiratory solenoid, it was necessary to choose a device with a sufficiently high valve flow coefficient (Cv) which could still actuate quickly enough to enable robust control of the gas flow. A reduced Cv in this portion of the circuit would restrict the ability of the patient to exhale. Initially, a number of control valves were sourced for their rapid switching speeds and empirically tested, as Cv estimates are often not provided by valve manufacturers. Ultimately, however, we selected a process valve in lieu of a control valve to ensure the device would flow sufficiently well, and the choice of valve did not present problems when implementing the control strategy. The SMC VXZ250HGB solenoid valve in the normally-open configuration was selected. The valve in particular was sourced partially due to its large port size (3/4" NPT). If an analogous solenoid with rapid switching speed and large Cv cannot be sourced, engineers replicating our device may consider the use of pneumatically actuated valves driven from air routed from a take-off downstream of the pressure regulator. 

**Manual PEEP valve sourcing.**
The PEEP valve is one of the few medical-specific COTS components in the device. The system configuration assumes the use of any ventilator-specific PEEP valve (Teleflex, CareFusion, etc.) coupled with an adapter to the standard 22 mm respiratory circuit tubing. In anticipation of potential supply chain limitations, as noted previously, we additionally provide the CAD models of a 3D printable PEEP valve. 

Sensor Selection
---------------------
We selected a minimal set of sensors with analog outputs to keep the system design sufficiently adaptable. If there were a part shortage for a specific pressure sensor, for example, any readily available pressure sensor with an analog output could be substituted into the system following a simple adjustment in calibration in the controller. Our system uses three sensors: an oxygen sensor, an airway pressure sensor, and a flow sensor with availability for a fourth addition, all interfaced with the Raspberry Pi via a 4-channel ADC (Adafruit ADS1115) through an I2C connection.

**Oxygen sensor.**
We selected an electrochemical oxygen sensor (Sensironics SS-12A) designed for the range of FiO2 used for standard ventilation and in other medical devices. The cell is self-powered, generating a small DC voltage (13-16 mV) that is linearly proportional to oxygen concentration. The output signal is amplified by an instrumentation amplifier interfacing the sensor with the Raspberry Pi controller (see electronics). This sensor is a wear part with a lifespan of about 6 years under operation at ambient air; therefore under continuous ventilator operation with oxygen-enriched gas, it will need to be replaced more frequently. This part can be replaced with any other medical O2 sensor provided calibration is performed given that these parts are typically sold as raw sensors, with a 3-pin molex interface. Moreover, the sensor we specify is compatible with a range of medical O2 sensors, including the Analytical Industries PSR-11-917-M or the Puritan Bennett 4-072214-00, so we anticipate abundant sourcing options.

**Airway pressure sensor.**
We selected a pressure sensor with a few key characteristics in mind: 1) the sensor had to be compatible with the 5V supply of the Raspberry Pi, 2) the sensor's input pressure range had conform to the range of pressures possible in our device (up to 70 cm H2O, the pressure relief valve's cutoff), and 3) the sensor's response time had to be sufficiently fast. We selected the amplified middle pressure sensor from Amphenol (1 PSI-D-4V), which was readily available, with a measurement range up to 70 cm H2O and an analog output voltage span of 4 V. Moreover, the decision to utilize an analog sensor is convenient for engineers replicating the design, as new analog sensors can be swapped in without extensive code and electronics modifications, as in the case of I2C devices which require modifications to hardware addresses. Other pressure sensors from this Amphenol line can be used as replacements if necessary.

**Spirometer.**
Because flow measurement is essential for measuring tidal volume during pressure-controlled ventilation, medical flow sensor availability was extremely limited during the early stages of the 2020 COVID-19 pandemic, and supply is still an issue. For that reason, we looked for inexpensive, more easily sourced spirometers to use in our system. We used the GE D-Lite spirometer, which is a mass-produced part and has been used in hospitals for nearly 30 years. The D-Lite sensor is inserted in-line with the flow of gas on the expiratory limb, and two ports are used to measure the differential pressure drop resulting from flow through a narrow physical restriction. The third pressure-measurement port on the D-Lite is blocked by a male Luer cap, but this could be used as a backup pressure measurement port if desired. An Amphenol 5 INCH-D2-P4V-MINI was selected to measure the differential pressure across the two D-Lite takeoffs. As with the primary (absolute) pressure sensor, this sensor was selected to conform to the voltage range of the Raspberry Pi, operate within a small pressure range, and have a sufficiently fast response time (partially as a function of the analog-to-digital converter). Also, this analog sensor can be readily replaced with a similar analog sensor without substantial code/electronics modifications.

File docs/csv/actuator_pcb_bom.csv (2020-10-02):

Ref | Part | Purpose
J2 | 2-pin screw terminal, 5.08 mm pitch, PCB mount | Connects to 24V supply
J3 | 2-pin screw terminal, 5.08 mm pitch, PCB mount | Connects to on/off expiratory valve
J4 | 2-pin screw terminal, 5.08 mm pitch, PCB mount | Connects to inspiratory valve, driven by PWM
J5 | 40-pin stackable RPi header | Connects board to RPi
J6 | 2-pin 0.1" header | Jumper between 5V and Raspberry Pi
C1 | 6.8 uF, 50V | 24V rail filter cap
C2 | 6.8 uF, 50V | 24V rail filter cap
C3 | 100 uF, 16V | 5V rail filter cap
U1 | ULN2003A | Darlington BJT array to drive solenoids
U2 | CUI PDQ15-Q24-S5-D | 24-to-5V DC-DC converter

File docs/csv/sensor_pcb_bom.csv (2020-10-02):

Ref | Part | Purpose
J1 | 40-pin stackable RPi header | Connects board to RPi
J2 | 4-pin 0.1" header | I2C connector if desired
J3 | 2-pin 0.1" header | Connects ALRT pin from ADS1115 to RPi if needed
J4 | 3-pin 0.1" header or 3 pin fan extension cable | Connects board to oxygen sensor
R1 | 330 Ohm resistor | Sets gain for INA126
C1 | 10 uF, 25V | Cap for TL7660
C2 | 10 uF, 25V | Cap for TL7660
U1 | TL7660, DIP8 | Rail splitter for INA126
U2 | INA126, DIP8 | Instrumentation amplifier for oxygen sensor output
U3 | Amphenol 1 PSI-D-4V-MINI | Airway pressure sensor
U4 | Adafruit ADS1115 | 4x 12-bit ADC
U5 | Amphenol 5 INCH-D2-P4V-MINI | Differential pressure sensor (for flow measurement)
U6 |  | Auxiliary analog output sensor slot

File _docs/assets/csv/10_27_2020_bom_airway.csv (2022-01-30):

Component | Subtotal | Example Sourcing Link
Oxygen DISS to 3/8" NPT Adapter | $10.00 | www.mcmaster.com/2633N11/
Inlet manifold | $24.56 | https://www.mcmaster.com/1023N15/
1/4" NPT Connector (male/male) | $3.89 | https://www.mcmaster.com/1455N133/
Teflon tape | $2.62 | https://www.mcmaster.com/6802K12/
Manifold plug 1/4" NPT | $4.50 | https://www.mcmaster.com/1725K13/
Hex nuts | $3.77 | https://www.mcmaster.com/91841A195/
Manifold washers | $10.16 | https://www.mcmaster.com/92217A440/
Fixed pressure regulator | $47.94 | https://www.mcmaster.com/1777K2
Push-to-connect: 1/4" NPT | $10.96 | https://www.mcmaster.com/5225K715/
Pneumatic Tubing | $2.13 | https://www.mcmaster.com/50315K71
Push-to-connect: 1/8" BSPT | $10.76 | https://www.mcmaster.com/5225K305/
Insp proportional valve | $107.10 | https://www.ocpneumatics.com/smc-pvq31-5g-23-01n-h-valve-proportional-pvq-proportional-valve/
Push-to-connect: Inline T-adapter to 1/4" NPT | $7.58 | https://www.mcmaster.com/5225K806/
1/4" NPT Connector (female/female) | $9.84 | https://www.mcmaster.com/4589K58/
Pressure release valve | $19.89 | https://www.mcmaster.com/4277T52
Oxygen sensor | $59.00 | https://www.sensoronics.com/products/ss-12a-replaces-teledyne-r22-msa-472062
Emergency breathing (check) valve | $1.05 | https://serfinitymedical.com/products/teleflex-medical-one-way-valve-teleflex-medical-1665
DAR filters | $3.44 | https://www.bettymills.com/dar-electrostatic-filter-large-350u5865
Adult Respiratory Circuit w Humidifier Limb | $13.00 | Circuit: https://orsupply.com/product/1505
Gas sampling line | $5.01 | https://heymedsupply.com/gas-sampling-line-mckesson-16-gsl-each-1/
Luer lock connector | $20.50 | https://www.grainger.com/product/36T564?cm_mmc=PPC:+Google+PLA&s_kwcid=AL!2966!3!281698275999!!!g!470577457359!
Luer lock filter |  | https://catalog.promepla.com/promepla-component/ecb15992 / https://catalog.promepla.com/uploads/medias/plan-ecb15992.pdf
Pressure sensor (for Paw) | $32.00 | https://www.mouser.com/ProductDetail/Amphenol-All-Sensors/1-PSI-D1-4V-MINI?qs=BhOZL0NmoSxcjJYCCg1Awg%3D%3D
Tubing connectors | $14.00 | https://www.rcmedical.com/viewProduct.cfm?productID=591
Flow sensor | $4.76 | https://jakenmedical.com/supplies-accessories/disposable-d-lite-sensor-50-box-896952/
Luer plug | $2.60 | https://www.mcmaster.com/51525K311
Luer lock connector for D-Lite | $22.68 | https://www.mcmaster.com/5194K32/
Differential pressure sensor for flow | $52.70 | https://www.mouser.com/ProductDetail/Amphenol-All-Sensors/5-INCH-D2-P4V-MINI
3/4" NPT Connector (male/male) | $3.06 | https://www.mcmaster.com/46825K31/
Exp solenoid valve | $115.10 | https://www.smcpneumatics.com/VXZ250HGB.html
Exp solenoid brackets | $22.44 | https://www.mcmaster.com/3136N157/

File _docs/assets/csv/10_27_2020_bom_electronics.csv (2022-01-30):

Component | Subtotal | Example Sourcing Link
Standoffs | $3.76 | https://www.mouser.com/ProductDetail/Keystone-Electronics/24424
Meanwell DC Power Supply | $30.66 | https://www.mouser.com/ProductDetail/MEAN-WELL/NDR-120-24
DIN Rail | $7.74 | https://www.mcmaster.com/8961K17/
DIN washers | $13.94 | https://www.mcmaster.com/98025A029/
Sensor board (excluding pressure sensors)
2-layer PCB | $99.00 | https://www.4pcb.com/pcb-prototype-2-4-layer-boards-specials.html
12-bit ADC | $10.00 | https://www.mouser.com/ProductDetail/Adafruit/1083?qs=GURawfaeGuCmI2li4B6pKg%3D%3D
Voltage splitter U1 | $2.00 | https://www.digikey.com/product-detail/en/texas-instruments/TL7660CP/296-21857-5-ND/1629031
Instrumentation amplifier U2 | $4.00 | https://www.digikey.com/product-detail/en/texas-instruments/INA126PA/INA126PA-ND/300992
R3, sensor | $0.00
40 pin Pi header J1 | $3.00 | https://www.digikey.com/product-detail/en/adafruit-industries-llc/1979/1528-1783-ND/6238003
4x1 header J2 | $5.00 | https://www.digikey.com/product-detail/en/adafruit-industries-llc/4150/1528-2922-ND/10123801
2x1 header J3 | $5.00
Oxygen sensor cable (J4) | $2.00 | https://www.coolerguys.com/products/3-pin-fan-cable-extension-12-thru-72-inches?variant=17666421509
330 Ohm resistor R1 | $1.00 | https://www.digikey.com/product-detail/en/stackpole-electronics-inc/CF14JT330R/CF14JT330RCT-ND/1830338
Capacitors C1,C2 | $1.00 | https://www.digikey.com/product-detail/en/panasonic-electronic-components/ECA-1EM100B/P19522CT-ND/6109420
Actuator board
2-layer PCB | $99.00 | https://www.4pcb.com/pcb-prototype-2-4-layer-boards-specials.html
5V DC/DC Converter | $20.00 | https://www.mouser.com/ProductDetail/CUI-Inc/PDQE15-Q24-S5-D
Darlington array U1 | $2.00 | https://www.mouser.com/ProductDetail/Texas-Instruments/ULN2003AN?qs=FOlmdCx%252BAA1wYQ1G8c8hpQ%3D%3D
40 pin Pi header J1 | $3.00 | https://www.digikey.com/product-detail/en/adafruit-industries-llc/1979/1528-1783-ND/6238003
Screw terminals J2, J3, J4 | $4.00 | https://www.digikey.com/product-detail/en/te-connectivity-amp-connectors/282837-2/A113320-ND/2187973
2x1 header J5 | $5.00
Capacitor C1 | $1.00 | https://www.digikey.com/product-detail/en/panasonic-electronic-components/EEU-FR1C101B/P15330CT-ND/3072210
Capacitors C2,C3 | $1.00 | https://www.digikey.com/product-detail/en/panasonic-electronic-components/EEA-GA1H6R8/P14509-ND/2504598
Speaker | $20.00 | https://www.amazon.com/Z50-smartphone-tablet-laptop-Grey/dp/B00EZ9XLF8?hvadid=78408975043567&hvbmt=be&hvdev=c&hvqmt=e
TOTAL | $347

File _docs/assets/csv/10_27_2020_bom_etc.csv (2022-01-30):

Component | Subtotal | Example Sourcing Link
PETG for 3d printing | $30.00
Commercial PEEP valves
Adult Test Lung |  | https://www.ebay.com/itm/Adult-Test-Lung-LNG600P-Newport-Medical-Instruments-a-division-of-Covidien/264679192553
Air compressor for initial testing |  | https://www.dewalt.com/products/storage-and-gear/air-compressors/16-hp-continuous-225-psi-45-gallon-compressor/d55146

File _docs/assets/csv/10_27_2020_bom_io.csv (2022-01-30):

Component | Subtotal | Example Sourcing Link
Raspberry Pi | $53.00 | https://www.mouser.com/ProductDetail/Raspberry-Pi/RPI4-MODBP-2GB-BULK
USB-C Charger/cable | $9.88 | https://www.mouser.com/ProductDetail/Seeed-Studio/106990291?qs=sGAEpiMZZMtyU1cDF2RqUIiI0Dr66jYXGV7bLfwtXvw%3D
Micro SD Card | $8.29 | https://www.amazon.com/dp/B073JWXGNT/ref=twister_B07B3MFBHY?_encoding=UTF8&th=1
7" Display | $249.18 | https://lilliputdirect.com/lilliput-779gl-capacitive-touchscreen-hdmi-monitor?search=779gl
Screen Mount | $6.00 | https://lilliputdirect.com/lilliput-monitor-accessories/mounting-brackets-stands-and-arms/lilliput-monitor-stand
HDMI for Display | $19.59 | https://www.mouser.com/ProductDetail/molex/68786-0001/?qs=ASaot9jrY6HVNv%2F8Wfc2rQ%3D%3D&countrycode=US&currencycode=USD
Mini USB for Display | $5.49 | https://www.mouser.com/ProductDetail/matrix-orbital/extmusb3ft/?qs=4ybA1OVEHcjRr1VgZWmnlw%3D%3D&countrycode=US&currencycode=USD
Cable grommet | $10.08 | https://www.mcmaster.com/9307K61/
Cable P-clip | $7.00 | https://www.mcmaster.com/3225T63/
Keyboard | $49.99 | https://m.cdw.com/product/adesso-easy-touch-mini-trackball-keyboard/1839486
 | $8.15 | https://www.grainger.com/product/1FD82?gucid=N:N:FPL:Free:GGL:CSM-1946:tew63h3:20501231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
Power strip | $3.63 | https://www.parts-express.com/parts-express-3-outlet-strip-with-3-ft-cord-ul-black--125-406
TOTAL | $419

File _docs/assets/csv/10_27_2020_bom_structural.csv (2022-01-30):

Component | Subtotal | Example Sourcing Link
80/20 (x4) | $42.28 | https://www.mcmaster.com/47065T101
80/20 gusset bracket (x18) | $117.72 | https://www.mcmaster.com/47065T663
80/20 rail (x6) | $35.04 | https://www.mcmaster.com/47065T101
80/20 button head nuts (packs of 25, x2) | $11.24 | https://www.mcmaster.com/47065T905/
Button-head hex screws, pack of 50 | $6.03 | https://www.mcmaster.com/92949A833/
Socket head screw, pack of 100 | $9.66 | https://www.mcmaster.com/91292A111/
Button head screws (long), pack of 10 | $2.65 | https://www.mcmaster.com/92949A275/
Button head screws (short), pack of 25 | $8.40 | https://www.mcmaster.com/92095A239/
HDPE sheeting | $21.28 | https://www.mcmaster.com/8619K423
Lifting handle | $28.76 | https://www.mcmaster.com/5190A21/
Screws for lifting handle | $9.69 | https://www.mcmaster.com/91274A164/
Leveling mount (4 feet) | $1.89 | https://www.mcmaster.com/23015T82/
Nuts for leveling mount | $4.41 | https://www.mcmaster.com/91847A029/
PETG for 3d printing | $30.00
TOTAL | $329

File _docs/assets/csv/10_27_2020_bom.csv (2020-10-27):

Component | Description | McMaster Part # (if applicable) | Category | Unit Qty | Pkg. Qty | Bulk Qty | Bulk Parts Cost | Unit Cost | Subtotal (Bulk Parts Cost) | Subtotal (Unit Parts Cost) | Sourcing Link
I/O
Raspberry Pi | Raspberry Pi- Model B-1 (1GB RAM) |  | Compute | 1 | 1 | 1 | $53.00 | $53.00 | $53.00 | $53.00 | https://www.mouser.com/ProductDetail/Raspberry-Pi/RPI4-MODBP-2GB-BULK
USB-C Charger/cable | To power the RPi |  | Compute | 1 | 1 | 1 | $9.88 | $9.88 | $9.88 | $9.88 | https://www.mouser.com/ProductDetail/Seeed-Studio/106990291?qs=sGAEpiMZZMtyU1cDF2RqUIiI0Dr66jYXGV7bLfwtXvw%3D
Micro SD Card | SanDisk Ultra 32GB MicroSDHC UHS-I Card with Adapter |  | Compute | 1 | 1 | 1 | $8.29 | $8.29 | $8.29 | $8.29 | https://www.amazon.com/dp/B073JWXGNT/ref=twister_B07B3MFBHY?_encoding=UTF8&th=1
7" Display | Lilliput 779GL-70NP/C/T - 7" HDMI Capacitive Touchscreen monitor |  | Compute | 1 | 1 | 1 | $249.18 | $249.18 | $249.18 | $249.18 | https://lilliputdirect.com/lilliput-779gl-capacitive-touchscreen-hdmi-monitor?search=779gl
Screen Mount | Lilliput Monitor Stand |  | Compute | 1 | 1 | 1 | $6.00 | $6.00 | $6.00 | $6.00 | https://lilliputdirect.com/lilliput-monitor-accessories/mounting-brackets-stands-and-arms/lilliput-monitor-stand
HDMI for Display | Display cable: HDMI Cables HDMI Cbl Assbly 1M Micro to STD |  | Compute | 1 | 1 | 1 | $19.59 | $19.59 | $19.59 | $19.59 | https://www.mouser.com/ProductDetail/molex/68786-0001/?qs=ASaot9jrY6HVNv%2F8Wfc2rQ%3D%3D&countrycode=US&currencycode=USD
Mini USB for Display | Display cable: USB Cables / IEEE 1394 Cables 3 ft Ext A-B Mini USB Cable |  | Compute | 1 | 1 | 1 | $5.49 | $5.49 | $5.49 | $5.49 | https://www.mouser.com/ProductDetail/matrix-orbital/extmusb3ft/?qs=4ybA1OVEHcjRr1VgZWmnlw%3D%3D&countrycode=US&currencycode=USD
Cable grommet | USER_INTERFACE_CABLE_GROMMET: Buna-N Rubber Grommets, for 1-3/8" Hole Diameter and 1/16" Material Thickness, 1" ID, pack of 10 | 9307K61 | Routing | 1 | 10 | 1 | $10.08 | $1.01 | $10.08 | $1.01 | https://www.mcmaster.com/9307K61/
Cable P-clip | USER_INTERFACE_CABLE_P-CLIP_0.375_ID_SS: Snug-Fit Vibration-Damping Loop Clamp, 304 Stainless Steel with Silicone Rubber Cushion, 3/8" ID, pack of 10, 17/64 mounting holes | 3225T63 | Routing | 2 | 10 | 1 | $7.00 | $0.70 | $7.00 | $1.40 | https://www.mcmaster.com/3225T63/
Keyboard | Adesso: Mini keyboard with trackball |  | Compute | 1 | 1 | 1 | $49.99 | $49.99 | $49.99 | $49.99 | https://m.cdw.com/product/adesso-easy-touch-mini-trackball-keyboard/1839486
 | AC Power Cable |  | Compute | 1 | 1 | 1 | $8.15 | $8.15 | $8.15 | $8.15 | https://www.grainger.com/product/1FD82?gucid=N:N:FPL:Free:GGL:CSM-1946:tew63h3:20501231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
Power strip | Mini power strip - 3 outlet power strip with 3 ft cord |  |  | 1 | 1 | 1 | $3.63 | $3.63 | $3.63 | $3.63 | https://www.parts-express.com/parts-express-3-outlet-strip-with-3-ft-cord-ul-black--125-406
 |  |  |  |  |  |  |  |  |  |  | Compute Cost | $419
Airway Components
 | CUSTOM_ID_RUBBER_GROMMET_FOR_0.5_HOLE_0.0625_MATL: Cut-to-Size Grommets, SBR Rubber, for 1/2" Hole and 1/16" Thickness, 1/64-3/8" ID, Pack of 10 | 2633N11 | Routing | 1 | 10 | 1 | $10.00 | $1.00 | $10.00 | $1.00 | www.mcmaster.com/2633N11/
Oxygen DISS to 3/8" NPT Adapter | (Not specified in assembly) |  | Tubing/Adapters
Inlet manifold | 1023N150_MANIFOLD_0.375_NPT_IN_0.25NPT_OUT : Straight-Flow Rectangular Manifold, 2 Outlets, 3/8 NPT Inlet x 1/4 NPT Outlet | 1023N15 | Tubing/Adapters | 1 | 1 | 1 | $24.56 | $24.56 | $24.56 | $24.56 | https://www.mcmaster.com/1023N15/
1/4" NPT Connector (male/male) | PIPE_STUB_0.25_NPT_SS_W_SEALANT: Standard-Wall 304/304L Stainless Steel Pipe Nipple with Sealant, Threaded on Both Ends, 1/4 NPT, 1-1/2" Long | 1455N133 | Tubing/Adapters | 1 | 1 | 1 | $3.89 | $3.89 | $3.89 | $3.89 | https://www.mcmaster.com/1455N133/
Teflon tape | PTFE thread sealant tape (1/2") | 6802K12 | Tubing/Adapters | 1 | 1 | 1 | $2.62 | $2.62 | $2.62 | $2.62 | https://www.mcmaster.com/6802K12/
Manifold plug 1/4" NPT | MANIFOLD_PLUG_0.25_NPT_SS: High-Pressure 347 Stainless Steel Pipe Fitting, Plug with Hex Drive, 1/4 NPT Male | 1725K13 | Tubing/Adapters | 1 | 1 | 1 | $4.50 | $4.50 | $4.50 | $4.50 | https://www.mcmaster.com/1725K13/
Hex nuts | LN_10-32_STAINLESS_18-8: 18-8 Stainless Steel Hex Nut, 10-32 Thread Size, pack of 100 | 91841A195 | Fixing and framing |  | 100 | 1 | $3.77 | $0.04 | $3.77 | $0.00 | https://www.mcmaster.com/91841A195/
Manifold washers | W_10_NARROW_0.406OD_316_SS: 18-8 Stainless Steel Washer for Soft Material, Number 10 Screw Size, Narrow ASME Designation, pack of 25 | 92217A440 | Fixing and framing |  | 25 | 1 | $10.16 | $0.41 | $10.16 | $0.00 | https://www.mcmaster.com/92217A440/
Fixed pressure regulator | Fixed-Pressure Compressed Air Regulator (with two plugs) , 50 psi | 1777K41 | Flow control | 1 | 1 | 1 | $47.94 | $47.94 | $47.94 | $47.94 | https://www.mcmaster.com/1777K2
Push-to-connect: 1/4" NPT | PUSH_CONNECT_8MM_0.25_NPTM: 1/4" NPT to push-to-connect 8mm tubing | 5225K715 | Tubing/Adapters |  | 1 | 2 | $5.48 | $5.48 | $10.96 | $0.00 | https://www.mcmaster.com/5225K715/
Pneumatic Tubing | Polyurethane tubing: Firm Polyurethane Rubber Tubing for Air and Water, 5 mm ID, 8 mm OD | 50315K71 | Tubing/Adapters | 3 | 1 | 3 | $0.71 | $0.71 | $2.13 | $2.13 | https://www.mcmaster.com/50315K71
Push-to-connect: 1/8" BSPT | PUSH_CONNECT_FITTING_8MM_TO_0.125_BPST: Push-to-Connect Tube Fitting for Air, Straight Adapter, 8 mm Tube OD x 1/8 BSPT Male | 5225K305 | Tubing/Adapters | 2 | 1 | 2 | $5.38 | $5.38 | $10.76 | $10.76 | https://www.mcmaster.com/5225K305/
Insp proportional valve | SMC PVQ31-5G-23-01N-H valve, proportional, PVQ PROPORTIONAL VALVE |  | Flow control | 1 | 1 | 1 | $107.10 | $107.10 | $107.10 | $107.10 | https://www.ocpneumatics.com/smc-pvq31-5g-23-01n-h-valve-proportional-pvq-proportional-valve/
Push-to-connect: Inline T-adapter to 1/4" NPT | PUSH_CONNECT_T_8MM_0.25_NPT: Push-to-Connect Tube Fitting for Air, Inline Tee Adapter, for 8 mm Tube OD x 1/4 NPT Male | 5225K806 | Tubing/Adapters | 1 | 1 | 1 | $7.58 | $7.58 | $7.58 | $7.58 | https://www.mcmaster.com/5225K806/
1/4" NPT Connector (female/female) | NPTF_0.25_X_0.25_NPTF_COUPLER: CPVC Pipe Fitting for Hot Water, Straight Connector, 1/4 NPT Thread Female | 4589K58 | Tubing/Adapters | 1 | 1 | 1 | $9.84 | $9.84 | $9.84 | $9.84 | https://www.mcmaster.com/4589K58/
Pressure release valve | Compact Nylon Pressure-Relief Valve for Air, 1 psi, 1/4 NPT Male | 4277T52 | Tubing/Adapters | 1 | 1 | 1 | $19.89 | $19.89 | $19.89 | $19.89 | https://www.mcmaster.com/4277T52
Oxygen sensor | O2 Sensor, SS-12A (or equivalents, e.g. Analytical Industries PSR-11-917-M) |  | Sensors | 1 | 1 | 1 | $59.00 | $59.00 | $59.00 | $59.00 | https://www.sensoronics.com/products/ss-12a-replaces-teledyne-r22-msa-472062
Emergency breathing (check) valve | Teleflex Medical One Way Valve |  | Flow control | 1 | 1 | 1 | $1.05 | $1.05 | $1.05 | $1.05 | https://serfinitymedical.com/products/teleflex-medical-one-way-valve-teleflex-medical-1665
DAR filters | DAR Electrostatic filters - Large (10x) (NEED A PRESCRIPTION TO ORDER) | Yes | Tubing/Adapters | 2 | 1 | 2 | $1.72 | $1.72 | $3.44 | $3.44 | https://www.bettymills.com/dar-electrostatic-filter-large-350u5865
Adult Respiratory Circuit w Humidifier Limb | Standard resp. circuit | Yes | Tubing/Adapters | 1 | 1 | 1 | $13.00 | $13.00 | $13.00 | $13.00 | Circuit: https://orsupply.com/product/1505
 | Adapter / filter to connect gas sampling lines to proximal side - TOM |  | Tubing/Adapters |  |  |  |  | #DIV/0! | $0.00
Gas sampling line | Gas Sampling Line McKesson 16-GSL Each/1 (x3) |  | Tubing/Adapters | 3 | 1 | 3 | $1.67 | $1.67 | $5.01 | $5.01 | https://heymedsupply.com/gas-sampling-line-mckesson-16-gsl-each-1/
Luer lock connector | Sensit Luer Lock Connector from Grainger |  | Tubing/Adapters | 2 | 1 | 2 | $10.25 | $10.25 | $20.50 | $20.50 | https://www.grainger.com/product/36T564?cm_mmc=PPC:+Google+PLA&s_kwcid=AL!2966!3!281698275999!!!g!470577457359!
Luer lock filter | Luer lock filter 0.2um from Promepla |  |  |  |  |  |  |  |  |  | https://catalog.promepla.com/promepla-component/ecb15992 / https://catalog.promepla.com/uploads/medias/plan-ecb15992.pdf
Pressure sensor (for Paw) | 1 PSI-D-4V-MINI |  | Sensors | 1 | 1 | 1 | $32.00 | $32.00 | $32.00 | $32.00 | https://www.mouser.com/ProductDetail/Amphenol-All-Sensors/1-PSI-D1-4V-MINI?qs=BhOZL0NmoSxcjJYCCg1Awg%3D%3D
Tubing connectors | Flexible Connector (Silicone Rubber) 22mm I.D. X 22mm I.D. (x6) |  | Tubing/Adapters | 2 | 1 | 2 | $7.00 | $7.00 | $14.00 | $14.00 | https://www.rcmedical.com/viewProduct.cfm?productID=591
Flow sensor | Disposable GE D-Lite flow sensor |  | Tubing/Adapters | 1 | 1 | 1 | $4.76 | $4.76 | $4.76 | $4.76 | https://jakenmedical.com/supplies-accessories/disposable-d-lite-sensor-50-box-896952/
Luer plug | Plastic Quick-Turn Tube Coupling, Nylon Plastic Caps for Plugs | 51525K311 | Tubing/Adapters | 1 | 10 | 1 | $2.60 | $0.26 | $2.60 | $0.26 | https://www.mcmaster.com/51525K311
Luer lock connector for D-Lite | Quick Turn Tube Coupling for Air - 316 Stainless Steel Socket Connector | 5194K32 | Tubing/Adapters | 1 | 1 | 1 | $22.68 | $22.68 | $22.68 | $22.68 | https://www.mcmaster.com/5194K32/
Differential pressure sensor for flow | 5 INCH-D2-P4V-MINI |  | Sensors | 1 | 1 | 1 | $52.70 | $52.70 | $52.70 | $52.70 | https://www.mouser.com/ProductDetail/Amphenol-All-Sensors/5-INCH-D2-P4V-MINI
3/4" NPT Connector (male/male) | Thick-Wall Polypropylene Pipe Fitting for Chemicals, Connector with Hex Body, 3/4 NPT Male | 46825K31 | Tubing/Adapters | 2 | 1 | 2 | $1.53 | $1.53 | $3.06 | $3.06 | https://www.mcmaster.com/46825K31/
Exp solenoid valve | SMC VXZ250HGB valve, 20A, NORMALLY OPEN, C37, Port 3/4 (NPT), Orifice 20 |  | Flow control | 1 | 1 | 1 | $115.10 | $115.10 | $115.10 | $115.10 | https://www.smcpneumatics.com/VXZ250HGB.html
Exp solenoid brackets | T-Slotted Framing, Silver Flush 90 Degree Angle Bracket for 1" High Rail | 3136N157 | Fixing and framing | 2 | 1 | 2 | $11.22 | $11.22 | $22.44 | $22.44 | https://www.mcmaster.com/3136N157/
Framing/Structural Components
80/20 (x4) | T-Slotted Framing, Single 4-Slot Rail, Silver, 1" High x 1" Wide, Solid, 3' Long - 4x | 47065T101 | Fixing and framing | 4 | 1 | 4 | $10.57 | $10.57 | $42.28 | $42.28 | https://www.mcmaster.com/47065T101
80/20 gusset bracket (x18) | Silver Gusset Bracket, 1" Long for 1" High Rail T-Slotted Framing x18 | 47065T663 | Fixing and framing | 18 | 1 | 18 | $6.54 | $6.54 | $117.72 | $117.72 | https://www.mcmaster.com/47065T663
80/20 rail (x6) | T-Slotted Framing, Single 4-Slot Rail, Silver, 1" High x 1" Wide, Solid, 1' Long x6 | 47065T101 | Fixing and framing | 6 | 1 | 6 | $5.84 | $5.84 | $35.04 | $35.04 | https://www.mcmaster.com/47065T101
80/20 button head nuts (packs of 25, x2) | End-feed single nuts for T-Slotted framing: T-Slotted Framing, End-Feed Single Nut, 1/4"-20 Thread | 47065T905 | Fixing and framing |  | 25 | 2 | $5.62 | $0.22 | $11.24 | $0.00 | https://www.mcmaster.com/47065T905/
Button-head hex screws, pack of 50 | BHCS_0.25-20x0.412_SS: 18-8 Stainless Steel Button Head Hex Drive Screw, 1/4"-20 Thread Size, 7/16" Long, Pack of 50 | 92949A833 | Fixing and framing |  | 50 | 1 | $6.03 | $0.12 | $6.03 | $0.00 | https://www.mcmaster.com/92949A833/
Socket head screw, pack of 100 | SHCS_M3_X_0.5_6MM_SS: 18-8 Stainless Steel Socket Head Screw, M3 x 0.5 mm Thread, 6 mm Long, pack of 100 | 91292A111 | Fixing and framing |  | 100 | 1 | $9.66 | $0.10 | $9.66 | $0.00 | https://www.mcmaster.com/91292A111/
Button head screws (long), pack of 10 | BHCS_10-32_X_2_SS: 18-8 Stainless Steel Button Head Hex Drive Screw, 10-32 Thread Size, 2" Long, pack of 10 | 92949A275 | Fixing and framing |  | 10 | 1 | $2.65 | $0.27 | $2.65 | $0.00 | https://www.mcmaster.com/92949A275/
Button head screws (short), pack of 25 | BHCS_M6_X_1_8MM_SS: Button Head Hex Drive Screw, Passivated 18-8 Stainless Steel, M6 x 1 mm Thread, 8mm Long, pack of 25 | 92095A239 | Fixing and framing |  | 25 | 1 | $8.40 | $0.34 | $8.40 | $0.00 | https://www.mcmaster.com/92095A239/
HDPE sheeting | Moisture-Resistant HDPE Sheet, 12" x 48" x 1/16" | 8619K423 | Fixing and framing | 2 | 1 | 2 | $10.64 | $10.64 | $21.28 | $21.28 | https://www.mcmaster.com/8619K423
Lifting handle | LIFTING_HANDLE: Oval Pull Handle, Unthreaded Hole, Black Aluminum, 4-9/16" Center-to-Center Width | 5190A21 | Fixing and framing | 2 | 1 | 2 | $14.38 | $14.38 | $28.76 | $28.76 | https://www.mcmaster.com/5190A21/
Screws for lifting handle | SHCS_0.25-20x0.75_Gr8_ASTM_F1136, pack of 50 | 91274A164 | Fixing and framing |  | 50 | 1 | $9.69 | $0.19 | $9.69 | $0.00 | https://www.mcmaster.com/91274A164/
Leveling mount (4 feet) | TLA_LEVELING_MOUNT: Light Duty Leveling Mount, 1" Long 1/4"-20 Threaded Stud, pack of 4 | 23015T82 | Fixing and framing | 1 | 4 | 1 | $1.89 | $0.47 | $1.89 | $0.47 | https://www.mcmaster.com/23015T82/
Nuts for leveling mount | LN_THIN_0.25-20_STAINLESS: 18-8 Stainless Steel Thin Hex Nut, 1/4"-20 Thread Size, pack of 100 | 91847A029 | Fixing and framing |  | 100 | 1 | $4.41 | $0.04 | $4.41 | $0.00 | https://www.mcmaster.com/91847A029/
PETG for 3d printing | ~1 kg spool of PETG |  | Tubing/Adapters | 1 | 1 | 1 | $30.00 | $30.00 | $30.00 | $30.00
 |  |  |  |  |  |  |  |  |  |  | Structural | $329
Electronics
Standoffs | Standoffs & Spacers M2.5 x 16mm HEX M/F BRASS 4.9mm A/F |  | Electronics | 8 | 1 | 8 | $0.47 |  | $3.76 | $3.76 | https://www.mouser.com/ProductDetail/Keystone-Electronics/24424
Meanwell DC Power Supply | DIN Rail Power Supplies 150W 24V 5A EN55022 Class B |  | Electronics | 1 | 1 | 1 | $30.66 |  | $30.66 | $0.00 | https://www.mouser.com/ProductDetail/MEAN-WELL/NDR-120-24
DIN Rail | Aluminum DIN 3 Rail, 10mm Deep, 1m Long | 8961K17 | Electronics | 1 | 1 | 1 | $7.74 |  | $7.74 | $0.00 | https://www.mcmaster.com/8961K17/
DIN washers | W_0.25_FLAT_THICK_GR8_YELLOW_ZINC: Zinc Yellow-Chromate Plated Steel Oversized Washer, Grade 8, for 1/4" Screw Size, 0.281" ID, 0.625" OD, package of 100 | 98025A029 | Electronics | 6 | 100 | 1 | $13.94 |  | $13.94 | $0.00 | https://www.mcmaster.com/98025A029/
Sensor board (excluding pressure sensors)
2-layer PCB | Advanced Circuits 2 layer board |  | Electronics | 1 | 3 | 3 | $33.00 |  | $99.00 | $33.00 | https://www.4pcb.com/pcb-prototype-2-4-layer-boards-specials.html
12-bit ADC | Adafruit Data Conversion IC Development Tools ADS1015 Breakout 12-Bit ADC |  | Electronics | 1 | 1 | 1 | $9.95 |  | $10.00 | $9.95 | https://www.mouser.com/ProductDetail/Adafruit/1083?qs=GURawfaeGuCmI2li4B6pKg%3D%3D
Voltage splitter U1 | TL7660, 8-DIP package |  | Electronics | 1 | 1 | 1 | $1.55 |  | $2.00 | $1.55 | https://www.digikey.com/product-detail/en/texas-instruments/TL7660CP/296-21857-5-ND/1629031
Instrumentation amplifier U2 | INA126PA, 8-DIP package |  | Electronics | 1 | 1 | 1 | $3.18 |  | $4.00 | $3.18 | https://www.digikey.com/product-detail/en/texas-instruments/INA126PA/INA126PA-ND/300992
R3, sensor |  |  |  |  |  |  |  |  | $0.00
40 pin Pi header J1 | Raspberry pi 40 pin stacking header |  | Electronics | 1 | 1 | 1 | $2.95 |  | $3.00 | $2.95 | https://www.digikey.com/product-detail/en/adafruit-industries-llc/1979/1528-1783-ND/6238003
4x1 header J2 | male pin header 1x04 P2.54mm |  | Electronics | 360 pins | 4 pins | 1 | $4.95 |  | $5.00 | $0.06 | https://www.digikey.com/product-detail/en/adafruit-industries-llc/4150/1528-2922-ND/10123801
2x1 header J3 | male pin header 1x02 P2.54mm |  | Electronics | 360 pins | 2 pins | 1 | $4.95 |  | $5.00 | $0.03
Oxygen sensor cable (J4) | 3 pin fan cable extension, 36", ribbon style |  | Electronics |  |  | 1 | $1.99 |  | $2.00 | $1.99 | https://www.coolerguys.com/products/3-pin-fan-cable-extension-12-thru-72-inches?variant=17666421509
330 Ohm resistor R1 | 330 Ohm resistor, through hole, 1/4 Watt |  | Electronics | 1 | 1 | 1 | $0.10 |  | $1.00 | $0.10 | https://www.digikey.com/product-detail/en/stackpole-electronics-inc/CF14JT330R/CF14JT330RCT-ND/1830338
Capacitors C1,C2 | 10 uF, 25V, electrolytic radial |  | Electronics | 1 | 1 | 1 | $0.21 |  | $1.00 | $0.21 | https://www.digikey.com/product-detail/en/panasonic-electronic-components/ECA-1EM100B/P19522CT-ND/6109420
Actuator board
2-layer PCB | Advanced Circuits 2 layer board |  | Electronics | 1 | 3 | 3 | $33.00 |  | $99.00 | $33.00 | https://www.4pcb.com/pcb-prototype-2-4-layer-boards-specials.html
5V DC/DC Converter | 490-PDQE15-Q24-S5-D |  | Electronics | 1 | 1 | 1 | $19.12 |  | $20.00 | $19.12 | https://www.mouser.com/ProductDetail/CUI-Inc/PDQE15-Q24-S5-D
Darlington array U1 | ULN2003AN IC PWR RELAY 7NPN 1:1 16DIP |  | Electronics | 1 | 1 | 2 | $0.66 |  | $2.00 | $1.32 | https://www.mouser.com/ProductDetail/Texas-Instruments/ULN2003AN?qs=FOlmdCx%252BAA1wYQ1G8c8hpQ%3D%3D
40 pin Pi header J1 | Raspberry pi 40 pin stacking header |  | Electronics | 1 | 1 | 1 | $2.95 |  | $3.00 | $2.95 | https://www.digikey.com/product-detail/en/adafruit-industries-llc/1979/1528-1783-ND/6238003
Screw terminals J2, J3, J4 | 5.08 mm pitch 2-pin screw terminal block connector, PCB mount |  | Electronics | 1 | 1 | 3 | $1.04 |  | $4.00 | $3.12 | https://www.digikey.com/product-detail/en/te-connectivity-amp-connectors/282837-2/A113320-ND/2187973
2x1 header J5 | male pin header 1x02 P2.54mm |  | Electronics | 360 pins | 2 pins | 1 | $4.95 |  | $5.00 | $0.03
Capacitor C1 | 100 uF, 16V, electrolytic radial |  | Electronics | 1 | 1 | 1 | $0.32 |  | $1.00 | $0.32 | https://www.digikey.com/product-detail/en/panasonic-electronic-components/EEU-FR1C101B/P15330CT-ND/3072210
Capacitors C2,C3 | 6.8 uF, 50V, electrolytic radial |  | Electronics | 1 | 1 | 2 | $0.20 |  | $1.00 | $0.40 | https://www.digikey.com/product-detail/en/panasonic-electronic-components/EEA-GA1H6R8/P14509-ND/2504598
Speaker | Logitech Z50 speaker |  | Electronics | 1 | 1 | 1 | $19.99 |  | $20.00 |  | https://www.amazon.com/Z50-smartphone-tablet-laptop-Grey/dp/B00EZ9XLF8?hvadid=78408975043567&hvbmt=be&hvdev=c&hvqmt=e
 |  |  |  |  |  |  |  |  |  |  | Electronics | $347
 |  |  |  |  |  | Total Cost (with screen and optional accessories) |  |  | $1,753.57 | $1,415.24
Specialized Tools
M16 tap | HSS Tap, Bottoming Chamfer, M16 x 1.0 mm Thread (for mounting O2 Sensor) | 26015A236 | Tools and testing |  |  | 1 | $46.63 |  | $47.00 |  | https://www.mcmaster.com/26015A236
1/4" NPT tap | Uncoated High-Speed Steel Pipe and Conduit Thread Tap High-Speed Steel, Plug Chamfer, 1/4 NPT, 2-7/16" Overall Length | 2525A173 | Tools and testing |  |  | 1 | $24.94 |  | $25.00 |  | https://www.mcmaster.com/2525A173-2525A173
3/4" NPT tap | Uncoated High-Speed Steel Pipe and Conduit Thread Tap: High-Speed Steel, Plug Chamfer, 3/4 NPT, 3-1/4" Overall Length | 2525A176 | Tools and testing |  |  | 1 | $70.16 |  | $71.00 |  | https://www.mcmaster.com/2525A176/
1/4"-28 tap | 1/4"-28 TPI (1/4" UNF) for filter mount |  | Tools and testing |  |  | 1 | $6.99 |  | $6.99 |  | https://www.mcmaster.com/26955A88/
Ingmar QuickLung Test Bellows | (Optional) variable resistance/compliance test lung for testing only |  | Tools and testing |  |  | 1 | $1,500.00 |  | $1,500.00 |  | https://www.ingmarmed.com/product/quicklung/
Not on the List:
PETG for 3d printing | ~1 kg spool of PETG |  | Tubing/Adapters |  |  | 1 | $30.00 |  | $30.00
Commercial PEEP valves | Alternative: Medium silicone film for printed PEEP valve: https://www.mcmaster.com/86045K58 |  | Flow control
Adult Test Lung | Standard adult test lung (Many options here) |  | Tools and testing |  |  |  | $30.00 |  |  |  | https://www.ebay.com/itm/Adult-Test-Lung-LNG600P-Newport-Medical-Instruments-a-division-of-Covidien/264679192553
Air compressor for initial testing |  |  |  |  |  |  |  |  |  |  | https://www.dewalt.com/products/storage-and-gear/air-compressors/16-hp-continuous-225-psi-45-gallon-compressor/d55146

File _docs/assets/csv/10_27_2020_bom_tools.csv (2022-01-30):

Component | Subtotal | Example Sourcing Link
M16 tap | $47.00 | https://www.mcmaster.com/26015A236
1/4" NPT tap | $25.00 | https://www.mcmaster.com/2525A173-2525A173
3/4" NPT tap | $71.00 | https://www.mcmaster.com/2525A176/
1/4"-28 tap | $6.99 | https://www.mcmaster.com/26955A88/
Ingmar QuickLung Test Bellows | $1,500.00 | https://www.ingmarmed.com/product/quicklung/

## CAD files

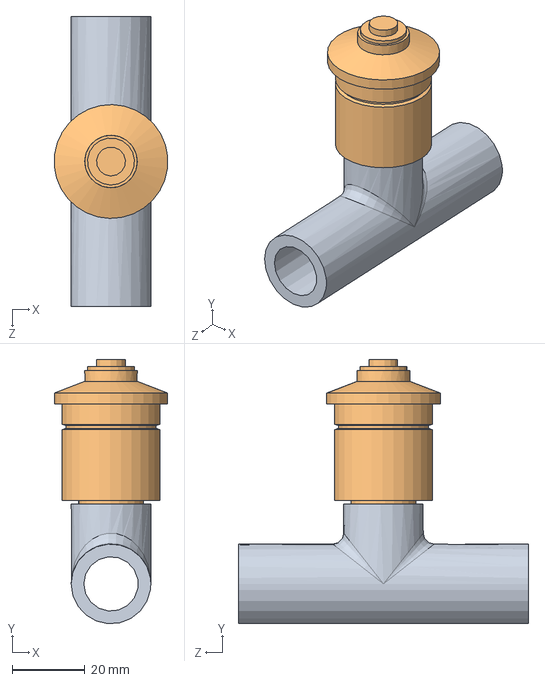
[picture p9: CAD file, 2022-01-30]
assets/solidworks/Parts/STD_TUBING_O2_SENSOR_ASSY.SLDASM
31.3 x 72.9 x 80.0 mm
O2_SENSOR_STD_TUBING_T_ADAPTER
O2_SENSOR_TYP_SS-11A

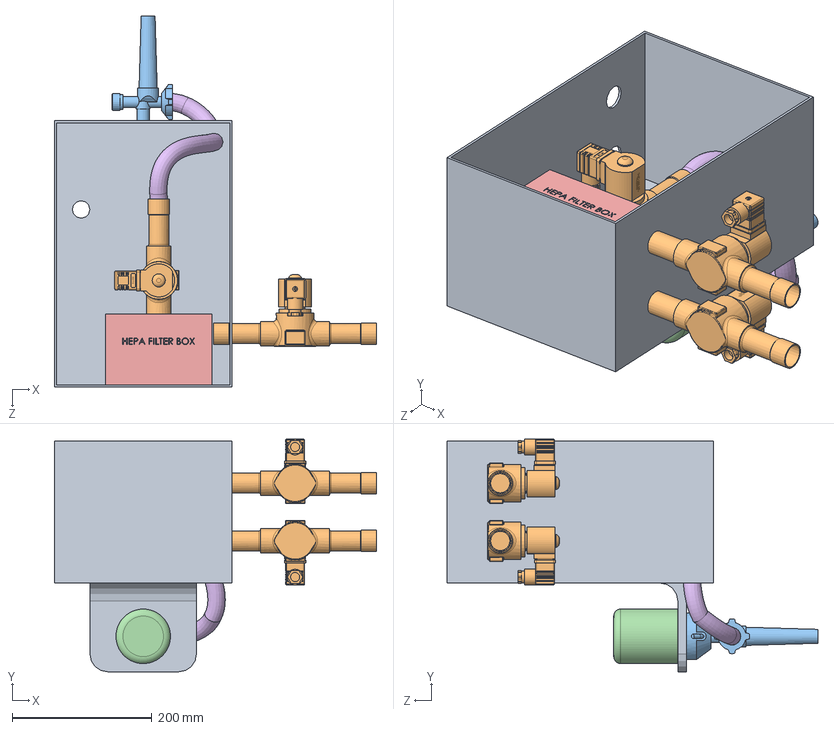
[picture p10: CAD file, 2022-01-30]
assets/solidworks/PVP1_Mk1.SLDASM
460.8 x 332.9 x 530.8 mm
AIR_BOX_TOTE_ASSY
200RD9T9 - 1.1-8S + BOBINA x 3
Flowmeter
humidifier
HEPA_FILTER_BOX
POST_FILTER_PRE_HUMIDIFIER_HOSE

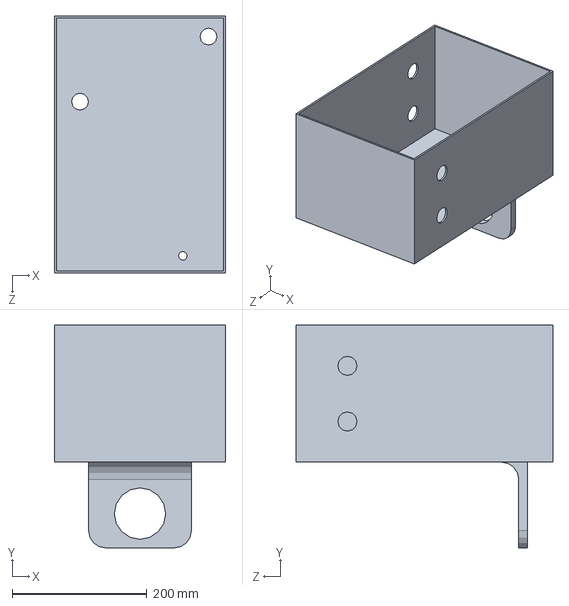
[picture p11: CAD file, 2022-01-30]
assets/solidworks/Parts/AIR_BOX_TOTE_ASSY.SLDPRT
254.0 x 330.2 x 381.0 mm

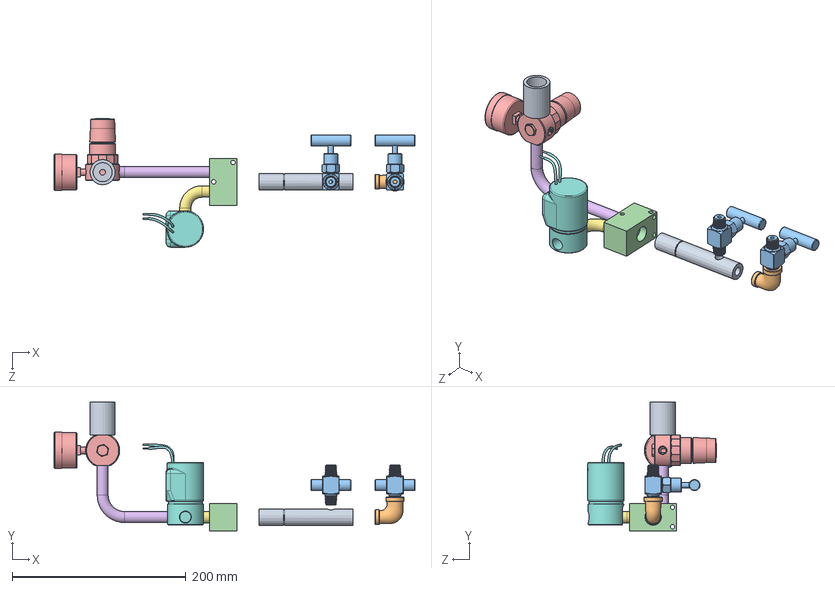
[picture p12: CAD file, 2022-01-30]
assets/solidworks/Parts/PNEUMATICS_INLET_ASSY.SLDASM
415.7 x 148.2 x 148.0 mm
VENTURI_MIXER_0.125_X_0.125X_0.25_NPTF
NPTF_ELBOW_REDUCER_0.125_X_0.25
MEDIUM_PRESSURE_NEEDLE_VALVE_0.25_NPTM x 2
NPTF_MANIFOLD_0.375_X_0.25_0.25
PRESSURE_REGULATOR_0.25_NPTF
MANIFOLD_TO_PRESSURE_REGULATOR_HOSE
MANIFOLD_TO_SOLENOID_TUBE
SOLENOID_VALVE_0.25_NPT_24V_STAINLESS
REGULATOR_TO_O2_SENSOR_ADAPTER

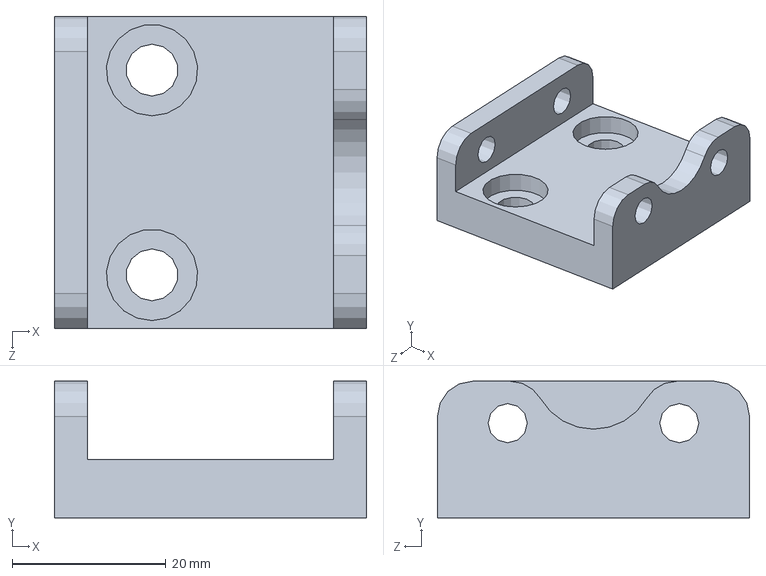
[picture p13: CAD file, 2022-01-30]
assets/solidworks/Parts/INLET_AIR_MAINFOLD_BRACKET_REV_2.SLDPRT
40.6 x 17.8 x 40.6 mm

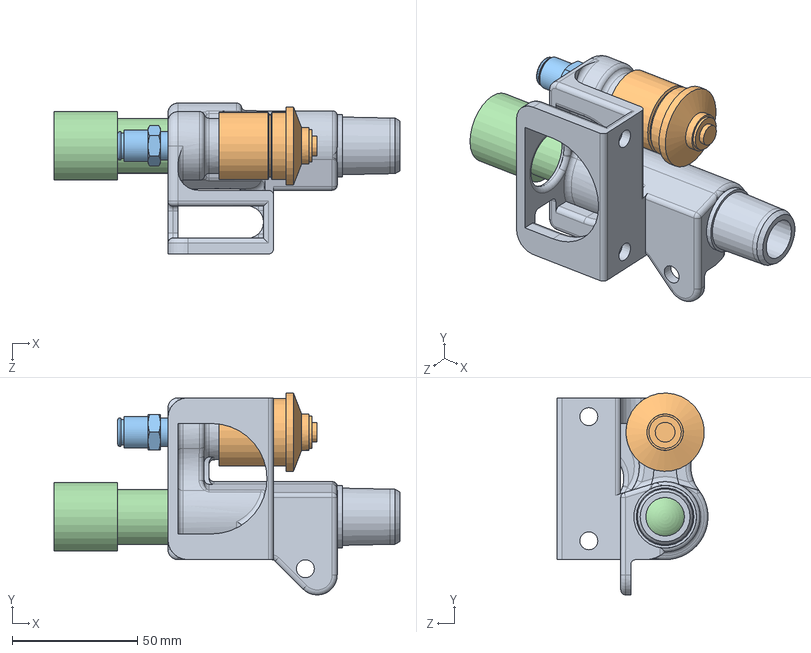
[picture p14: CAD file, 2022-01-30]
assets/solidworks/Parts/SENSOR_ATRIUM_ASSY_REV_2.SLDASM
137.9 x 80.5 x 60.2 mm
SENSOR_ATRIUM_V4
O2_SENSOR_TYP_SS-11A
PUSH_CONNECT_8MM_0.25_NPTM
Teleflex Medical One Way Valve - 1644

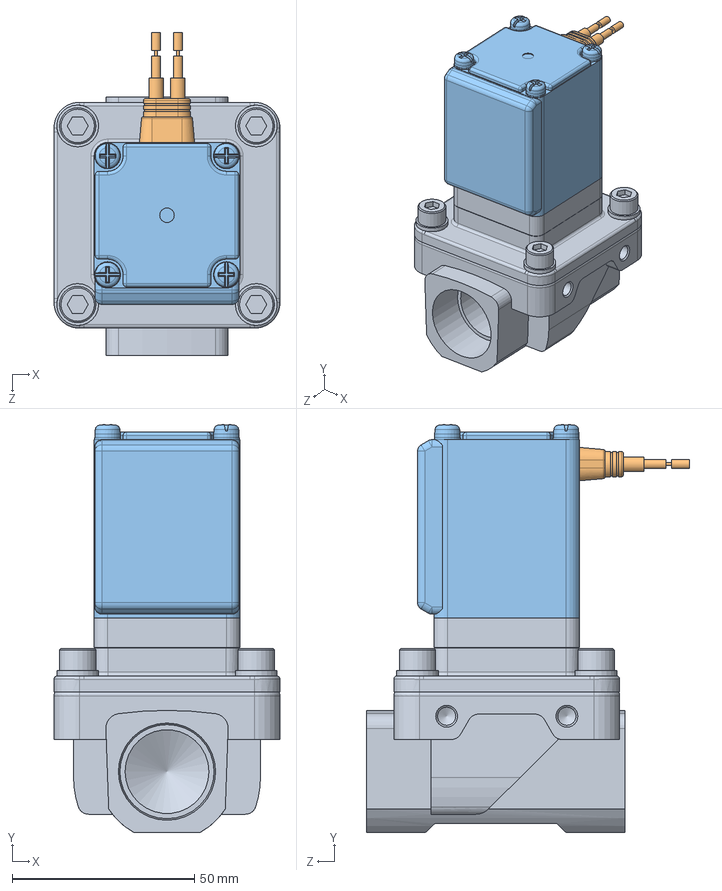
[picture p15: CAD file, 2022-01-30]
assets/solidworks/Parts/VXZ2C0HABXBB.SLDASM
62.0 x 112.0 x 88.7 mm
VXZ2C0HABXBB_C37_Body
VXZ2C0HABXBB_Grommet_1
VXZ2C0HABXBB_Solenoid_Coil

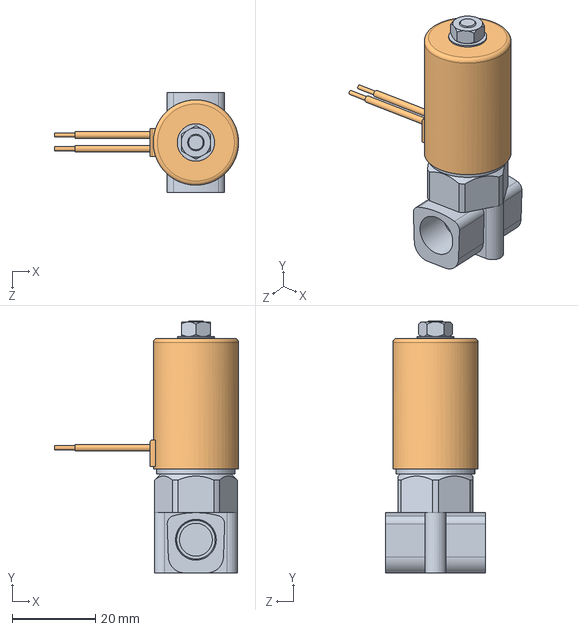
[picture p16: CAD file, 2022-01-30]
assets/solidworks/Parts/PVQ31-5G-23-01N.SLDASM
44.3 x 60.5 x 24.0 mm
PVQ31-5G-23-01N_PVQ30 Base
PVQ31-5G-23-01N_PVQ Body

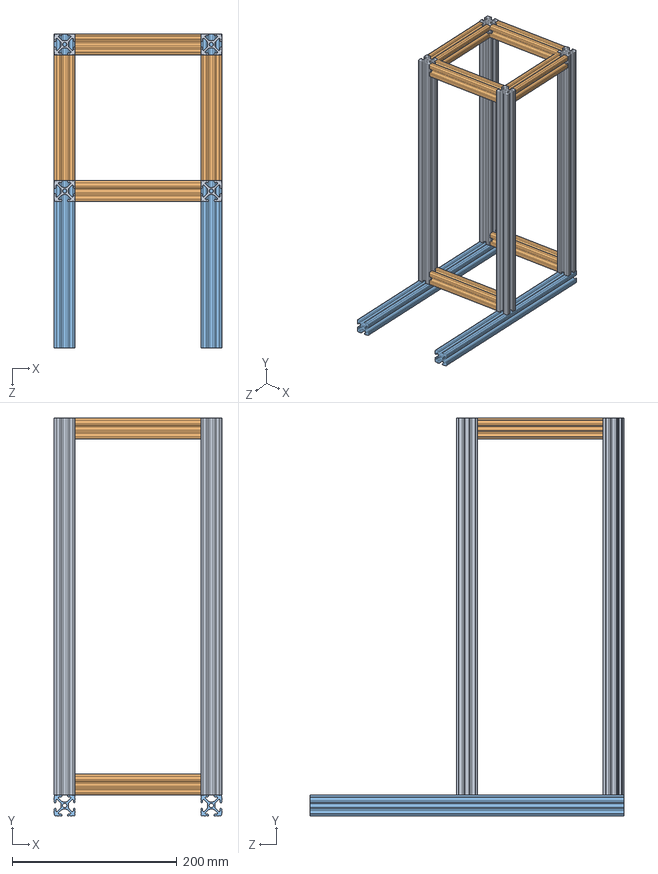
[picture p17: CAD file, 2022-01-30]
assets/solidworks/Parts/VENTILATOR_FRAME_REV_1.SLDASM
203.2 x 482.6 x 381.0 mm
EXTRUDED_ALUMINUM_1_X_1_VERTICAL_MEMBER x 4
EXTRUDED_ALUMINUM_1_X_1_HORIZONTAL_MEMBER x 6
EXTRUDED_ALUMINUM_1_X_1_LEG_MEMBER x 2

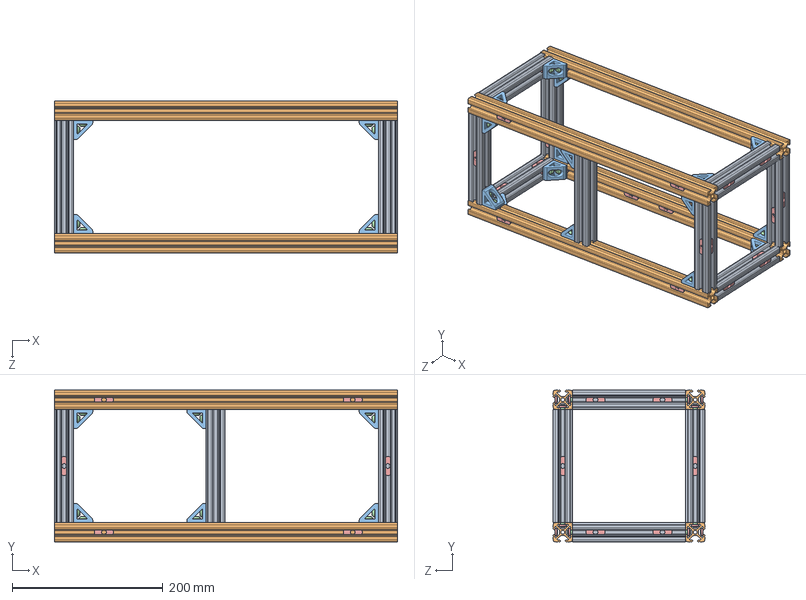
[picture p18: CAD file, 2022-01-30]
assets/solidworks/Parts/VENTILATOR_FRAME_V2.SLDASM
455.2 x 201.2 x 201.2 mm
EXTRUDED_ALUMINUM_1_X_1_HORIZONTAL_MEMBER x 9
EXTRUDED_ALUMINUM_1_X_1_VERTICAL_MEMBER x 4
AL_T-SLOT_1_IN_ANGLE_BRACKET_SINGLE x 18
BHCS_0.25-20x0.412_SS x 36
EXTRUDED_ALUMINUM_1_X_1_0.25-20_NUT x 71

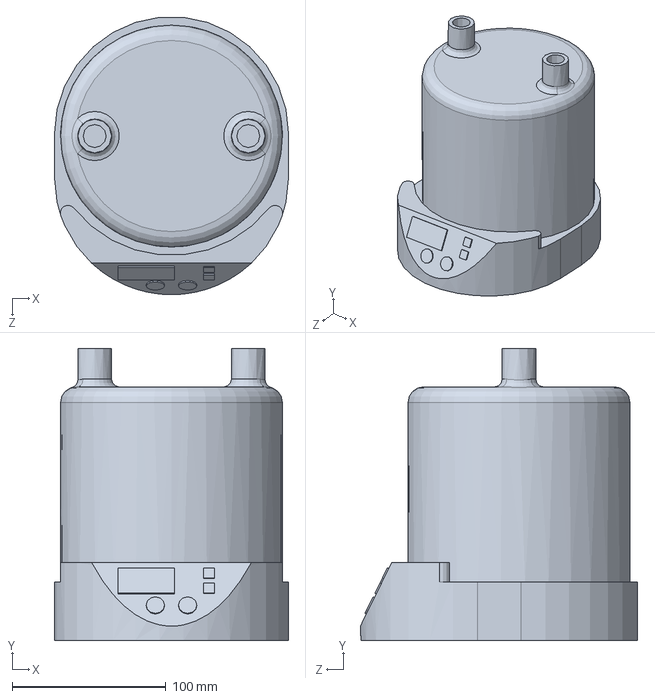
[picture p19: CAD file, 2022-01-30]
assets/solidworks/Parts/CPAP_BIPAP_HEATER_HUMIDIFIER_ASSY.SLDPRT
152.4 x 190.1 x 180.5 mm

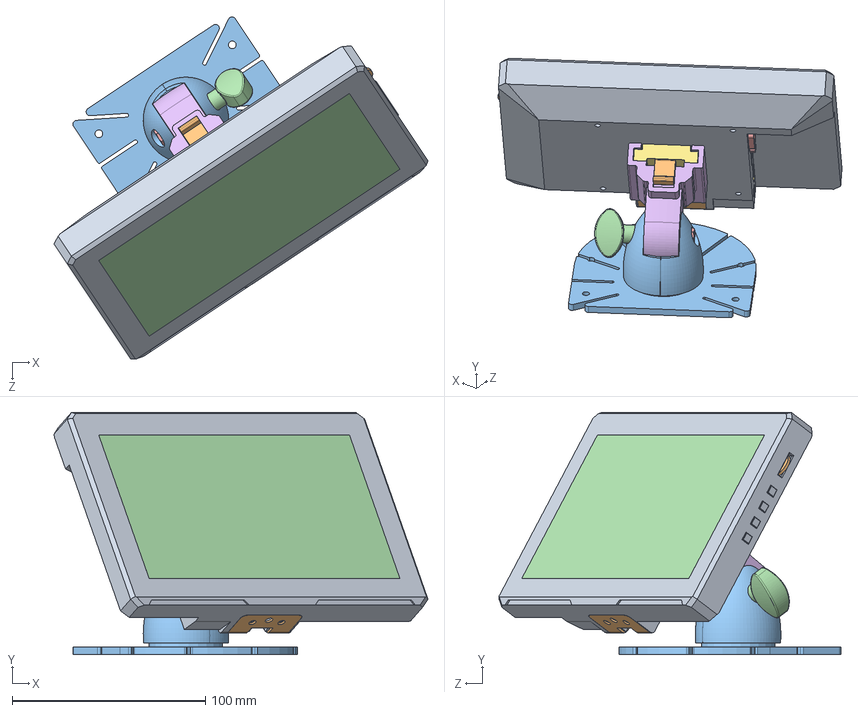
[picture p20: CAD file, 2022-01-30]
assets/solidworks/Parts/HDMI_TOUCHSCREEEN_MONITOR_7IN_MOUNTED_ASSY.SLDASM
193.6 x 125.3 x 177.1 mm
Lilliput 779GL-70NP-C-T 7 7 inch HDMI_1.stp
camera mount.stp
BS 4183 - M2,5 x 4.stp x 4
glass.stp
VGA adaptor.stp
HDMI.stp
connector.stp
12V DC adaptor.stp
knob.stp x 4
volume.stp
voeplaat opstand.stp
knop.stp
AS 1427 - M5 x 25.stp
houder.stp
klem.stp
AS 1427 - M5 x 10.stp
1.stp
2.stp
PHANTOM_BASE_7_IN_MONITOR

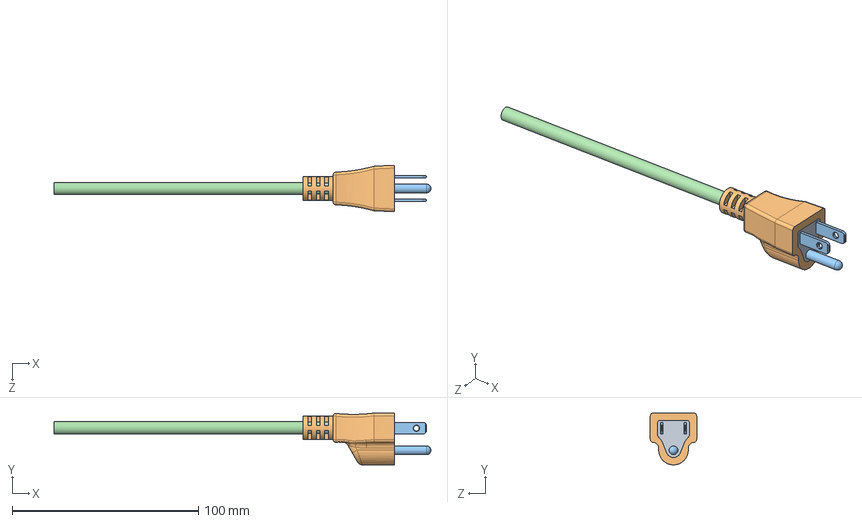
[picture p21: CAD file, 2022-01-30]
assets/solidworks/Parts/ac.plug.ASMBLY.SLDASM
202.6 x 27.9 x 25.0 mm
acplug.inner
ac.plug.surround
ac.plug.prongs^ac.plug.ASMBLY
ac.plug.wire

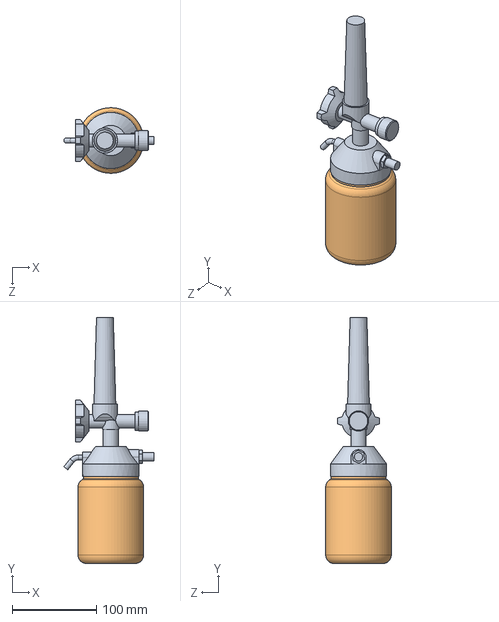
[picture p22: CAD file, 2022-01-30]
assets/solidworks/Parts/Flowmeter & Humidifier.SLDASM
107.3 x 292.3 x 78.0 mm
Flowmeter
humidifier

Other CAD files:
assets/solidworks/Parts/PRESSURE_REGULATOR_ASSY_PRG700.SLDASM
assets/solidworks/Parts/INLET_AIR_MAINFOLD_BRACKET.SLDPRT
assets/solidworks/Parts/MOUNTED_SCREEN_ASSY.SLDASM
assets/solidworks/Parts/3D_PRINTABLE_PEEP_VALVE.SLDASM
assets/DXFs/BOTTOM_PERFORATED_PANEL.DXF
assets/DXFs/FRONT_IP_PANEL_V1.DXF
assets/DXFs/REAR_IP_PANEL_V1.DXF
assets/DXFs/SIDE_IP_PANEL.DXF
assets/DXFs/TOP_IP_PANEL.DXF
assets/STLs/22MM_OD_TO_0.75_NPTM_ADAPTER.STL
assets/STLs/22MM_OD_TO_COMMERCIAL_PEEP_ADAPTER.STL
assets/STLs/All_PVP1_Components.3mf
assets/STLs/Alternative_Raspberry_Pi_DIN_Rail_Clip.stl
assets/STLs/EXPIRATORY_DAR_FILTER_BRACKET.STL
assets/STLs/EXPIRATORY_OUTLET_BRACKET_TO_PEEP_DVC.STL
assets/STLs/INLET_AIR_MAINFOLD_BRACKET_REV_2.STL
assets/STLs/INSPIRATORY_PROPORTIONAL_VALVE_BRACKET.STL
assets/STLs/IP_PANEL_VENT.STL
assets/STLs/LUER_LOCK_FILTER_MOUNT_V1.STL
assets/STLs/RASP_PI_DIN_RAIL_MOUNT_v3.STL
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

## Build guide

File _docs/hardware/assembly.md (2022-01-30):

# Assembly

**PVP1 Assembly Instructions**

- {download}`PDF Version </assets/PVP1 Assembly Instructions.pdf>`

This guide should help you assemble the ventilator from the parts found
in the [**Bill of Materials**](bom.rst):

We'll first show you how to assemble the hardware, then the electronics,
and finally put the two together.

Current Solidworks Assembly file:
- {download}`PVP1_Mk3.SLDASM </assets/solidworks/PVP1_Mk3.SLDASM>`

Prior Versions
- {download}`PVP1_Mk2.SLDASM </assets/solidworks/PVP1_Mk2.SLDASM>`
- {download}`PVP1_Mk1.SLDASM </assets/solidworks/PVP1_Mk1.SLDASM>`

All associated parts are available in the [solidworks/Parts](https://github.com/CohenLabPrinceton/pvp/tree/master/assets/solidworks/Parts) folder in the repository.

## Part 1. 3D Printed Components and Enclosure

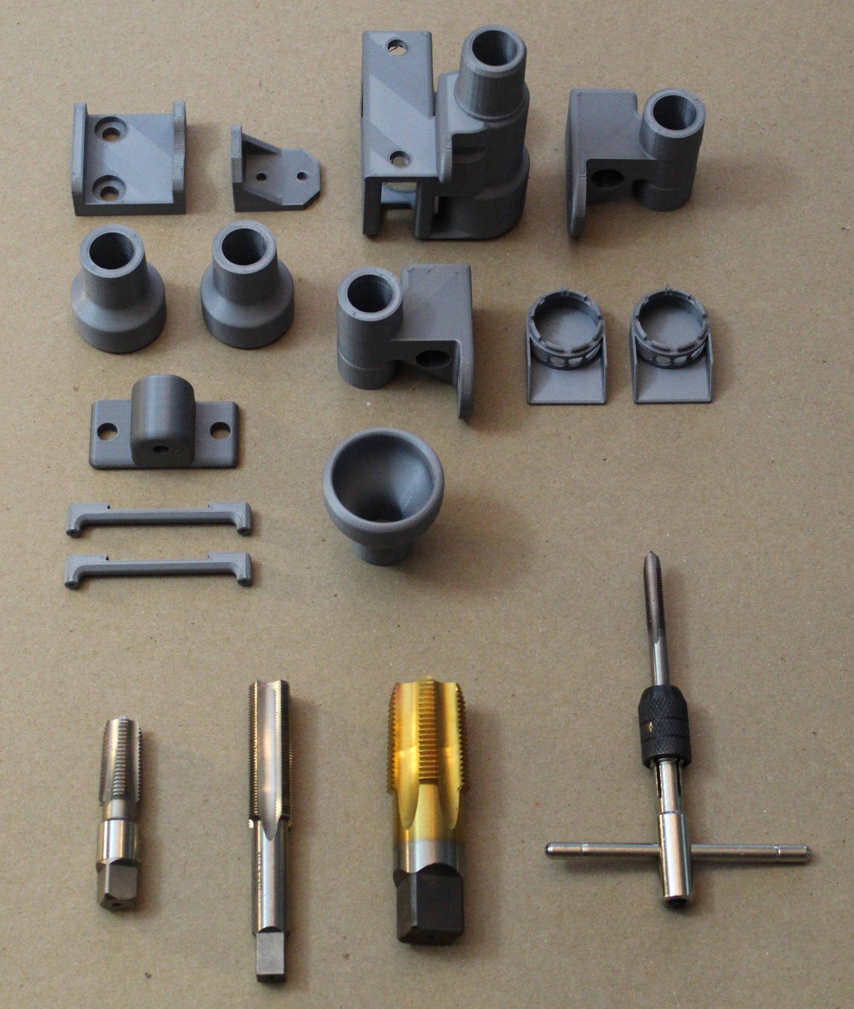
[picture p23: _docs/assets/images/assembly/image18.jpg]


### 1.1 3D Printing Adapters and Brackets.

Before we can get started with assembly, you'll need to print a few
parts using a standard 3D printer. (We ran our test prints on Prusa,
MakerBot, FlashForge, and Creality3D printers.)

[**You can download all the STL files from the CAD Page**](cad.rst)

Be sure to print airway components at as close to 100% infill as
possible, and be mindful of printing orientation. An example printing
setup is shown below. We do not recommend using supports or rafts unless
you find them to be necessary, as they are challenging to remove. If
there is a cylindrical channel, try to orient it vertically (such that
the circle is traced along the build plate), which will improve
circularity of the channel.

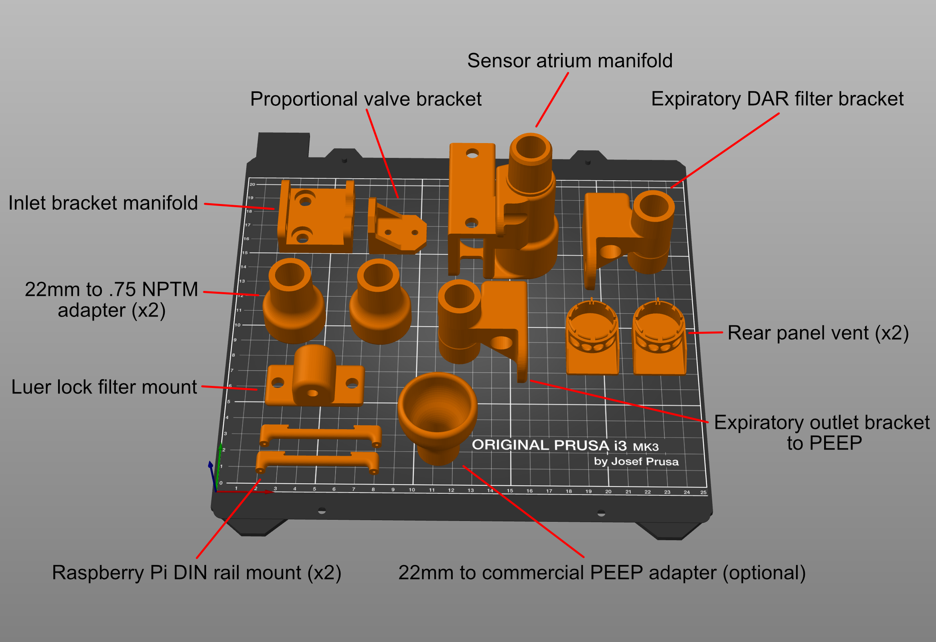
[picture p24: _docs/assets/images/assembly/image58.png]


If you are using a Prusa i3, **we also provide this print setup here**.

### 1.2 Tapping the 3D Printed Components

Several of the 3D printed parts will need to be tapped to enable
connection with other parts in the device- such as push-to-connect
adapters. You will be able to tap all of these parts by hand (since the
plastic cuts easily), and the [**Bill of Materials**](bom.rst) contains the list of
taps you will need, including specialized taps such as the M16.

All required taps are shown below:

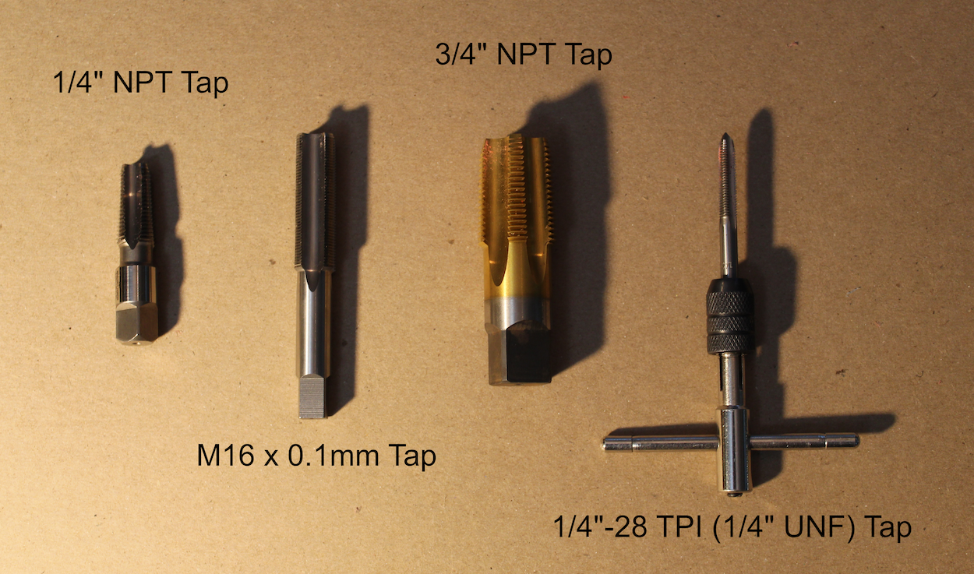
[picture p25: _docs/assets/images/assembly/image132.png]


First, we will tap the Sensor Atrium component, which houses the oxygen
sensor and "emergency breathing valve" check valve, and passes air from
the inspiratory limb to the respiratory circuit (with a DAR filter in
between).

**Step 1.** Use a ¼" NPT tap to thread the hole as shown below (the
smaller airway hole on the flat side of the Sensor Atrium), where a
push-to-connect adapter will attach.

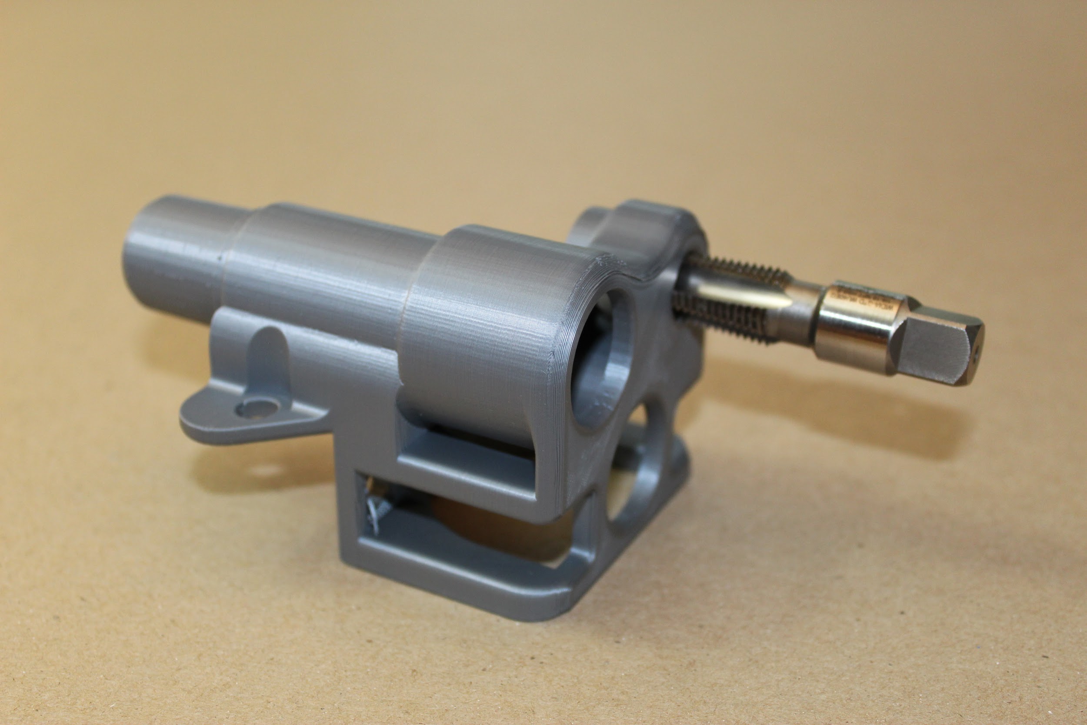
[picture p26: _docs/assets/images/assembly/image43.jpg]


**Step 2.** Use the M16 tap to thread the hole on the opposite side of
the Sensor Atrium, where the oxygen sensor will attach.

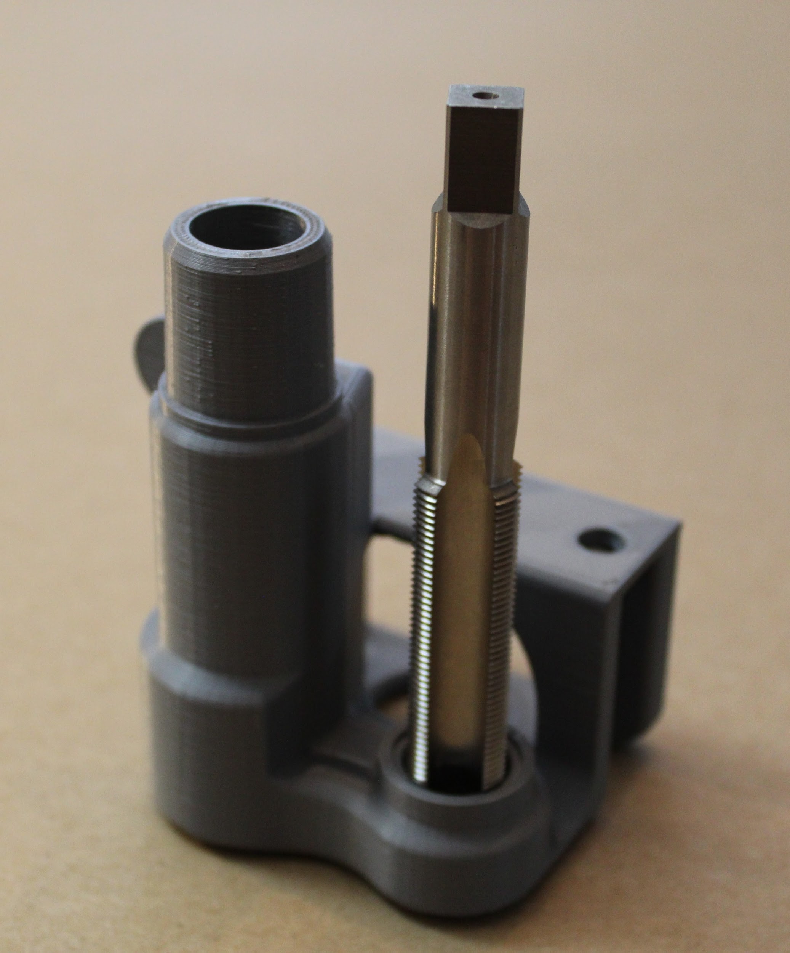
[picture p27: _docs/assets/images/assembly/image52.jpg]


Next, we will tap the adapters at either side of the expiratory
solenoid.

**Step 3.** Use the ¾" NPT tap to thread the holes on the larger end of
the two "22mm to 0.75 NPTM adapter" parts.

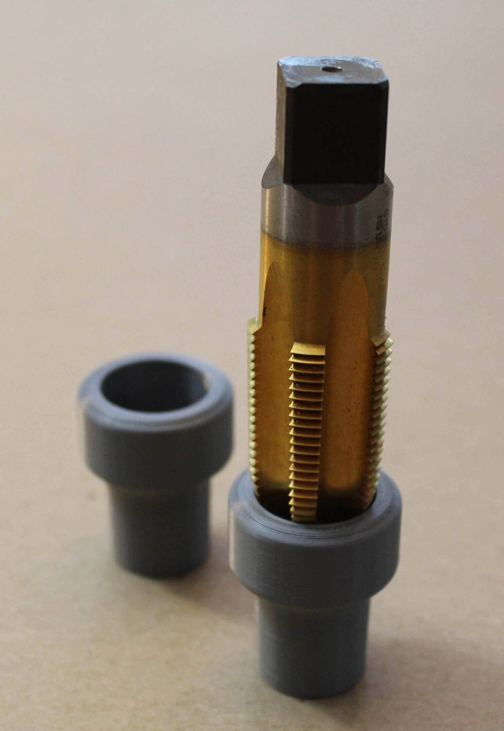
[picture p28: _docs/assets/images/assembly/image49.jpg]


Last, we will tap the adapter to the pressure sampling lines.

**Step 4.** Finally, use the ¼"-28 tap to thread the two airway holes on
the "Luer lock filter mount" part. These will hold the metal luer lock
adapters to the gas sampling lines for monitoring pressure.

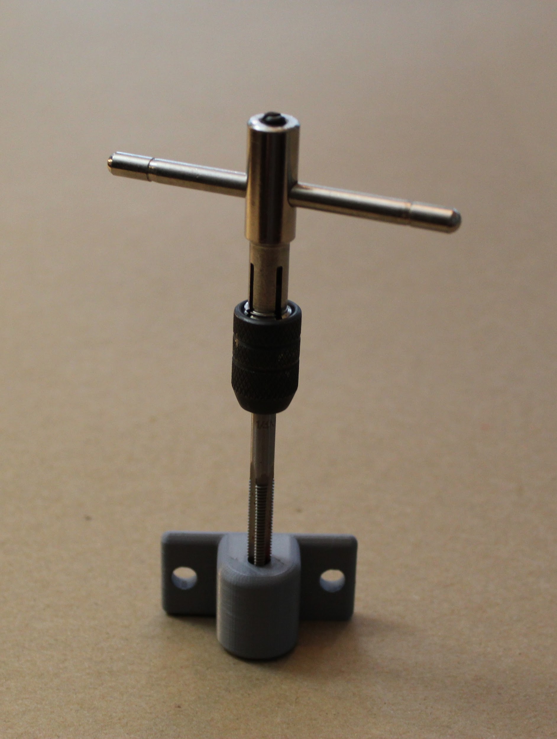
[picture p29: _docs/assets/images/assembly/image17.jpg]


### 1.3 Cutting Enclosure Pieces.

**Step 1. Laser cut, or cut out by hand, the six HPDE side panels.**

Cut all panels out of the 1/16" HPDE sheets. If you wish to cut these
pieces using a laser cutter, we provide DXF files in the [CAD Page](cad.rst), under
"Enclosure".

Cuts can also be made by hand using a sharp pair of scissors and a
razor-cutter. Pieces are 17 ⅞" by 7 ⅞" (45.4025 cm by 20.0025 cm), or 7
⅞" by 7 ⅞" (20.0025 cm by 20.0025 cm) along the outer dimensions.

(We cut our side panels for the demo out of acrylic for ease of
visibility.)

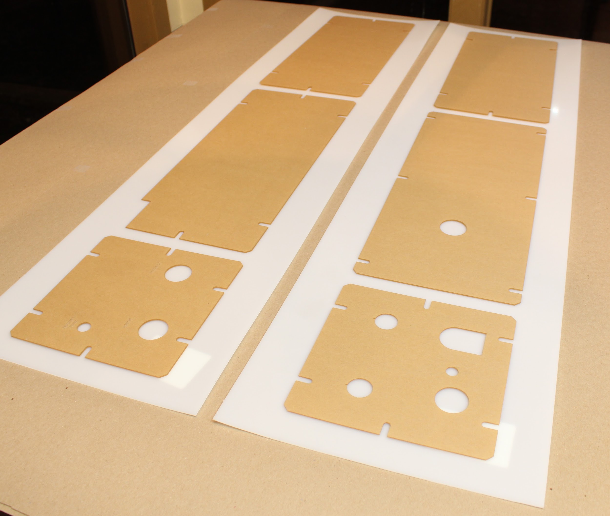
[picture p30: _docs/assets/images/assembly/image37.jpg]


**Step 2. Insert the rubber grommet(s).**

The bottom panel includes a hole for a large rubber grommet. Insert this
by hand.

If you wish, you may also insert a small custom grommet in the back
panel.

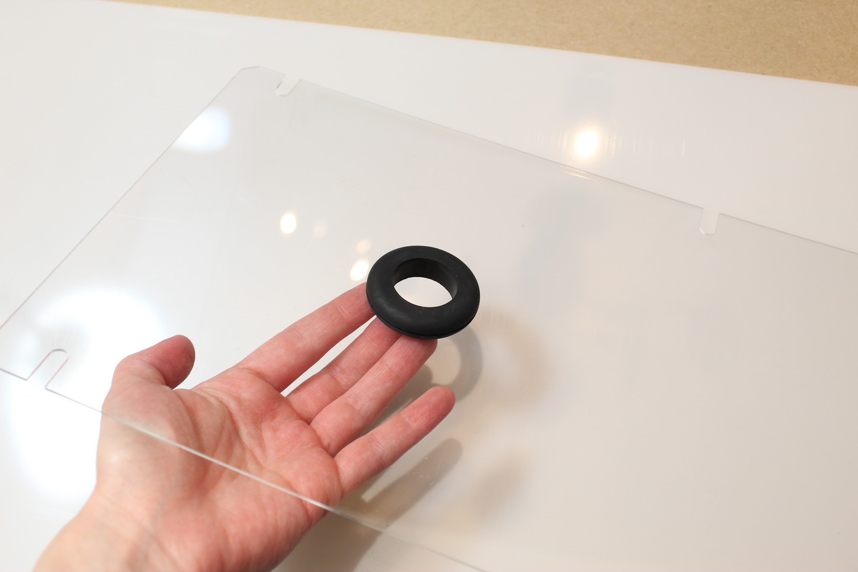
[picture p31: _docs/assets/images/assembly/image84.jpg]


## Part 2. Basic Hardware Assembly

### 2.1 Assembling the bottom frame

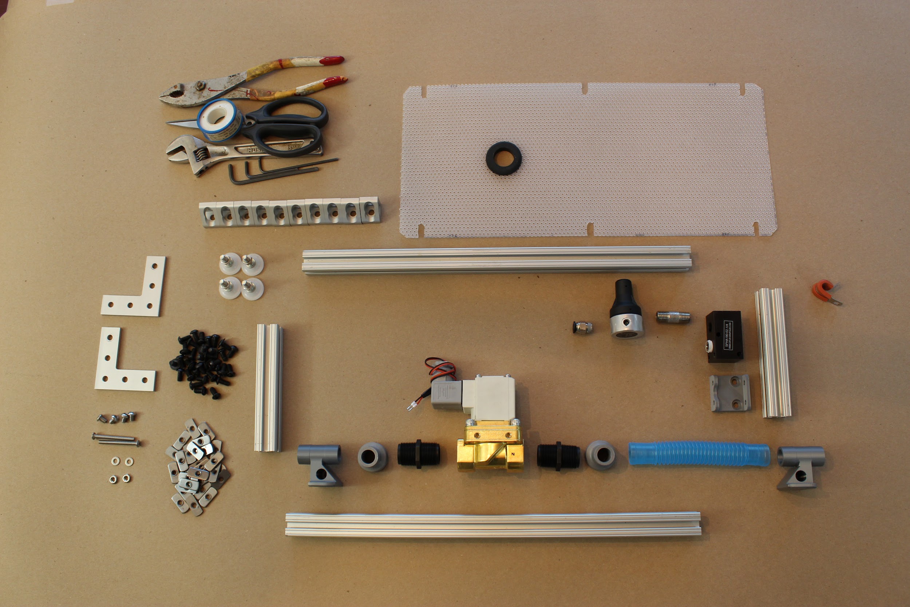
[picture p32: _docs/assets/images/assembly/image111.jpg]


**Step 1.** Cut the 80/20 ("T-slotted framing") to appropriately sized
pieces: In total, you will need 4 pieces of length 17 ⅞ in (45.4025 cm),
and 9 pieces of length 5 ⅞ in (14.9225 cm).

You can cut the aluminum 80/20 pieces by hand with a hack-saw, or using
machinery such as a bandsaw. Either way, be sure to file down any rough
edges afterward!

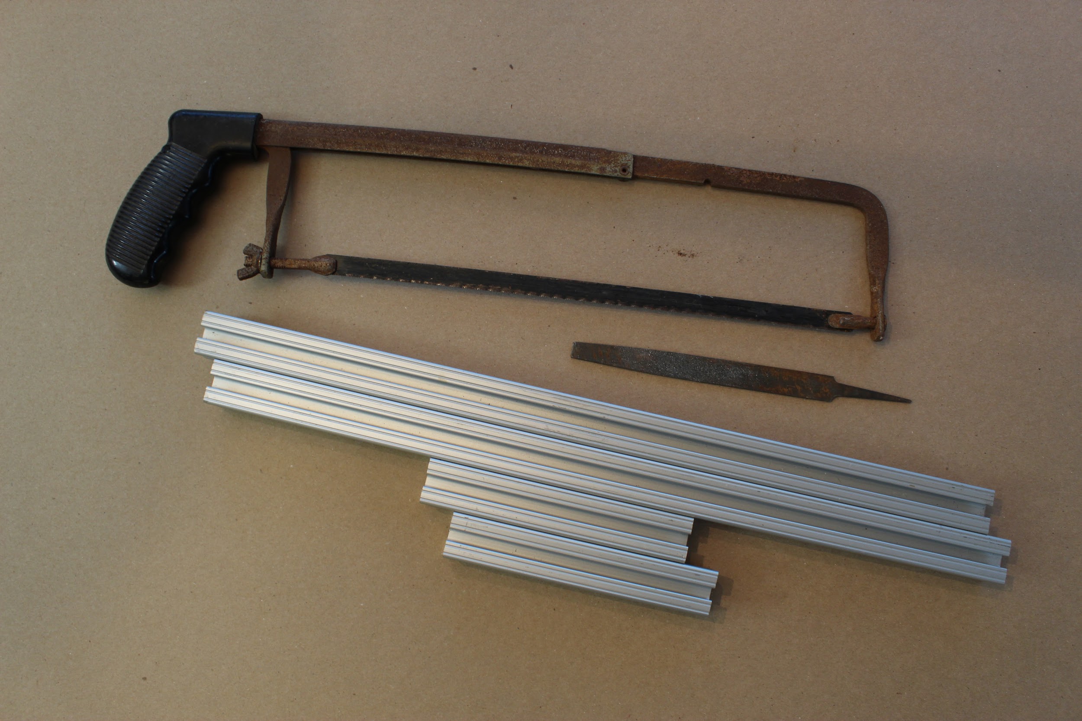
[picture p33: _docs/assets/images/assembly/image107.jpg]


**Step 2.** Attach the ¾" NPT (male-male) connectors to either side of
the expiratory solenoid, and then attach the two "22mm to .75 NPTM
adapter" parts to those, as shown. When attaching any airway threaded
parts in this assembly process, be sure to use PTFE thread sealant tape,
wrapping twice around the threads, in the direction shown (away from
your body if the threads are oriented towards the right).

(Note: From now on, we will not explicitly write out the need for Teflon
tape; be sure to use it whenever a threaded airway component is
involved!)

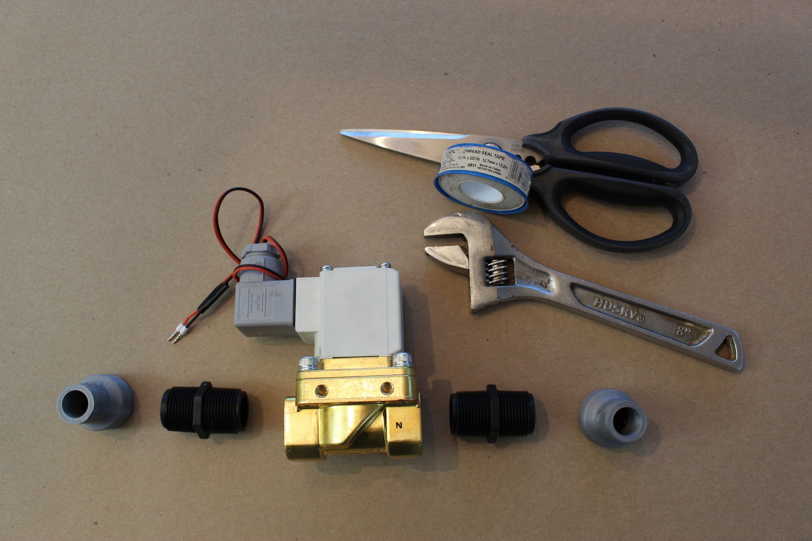
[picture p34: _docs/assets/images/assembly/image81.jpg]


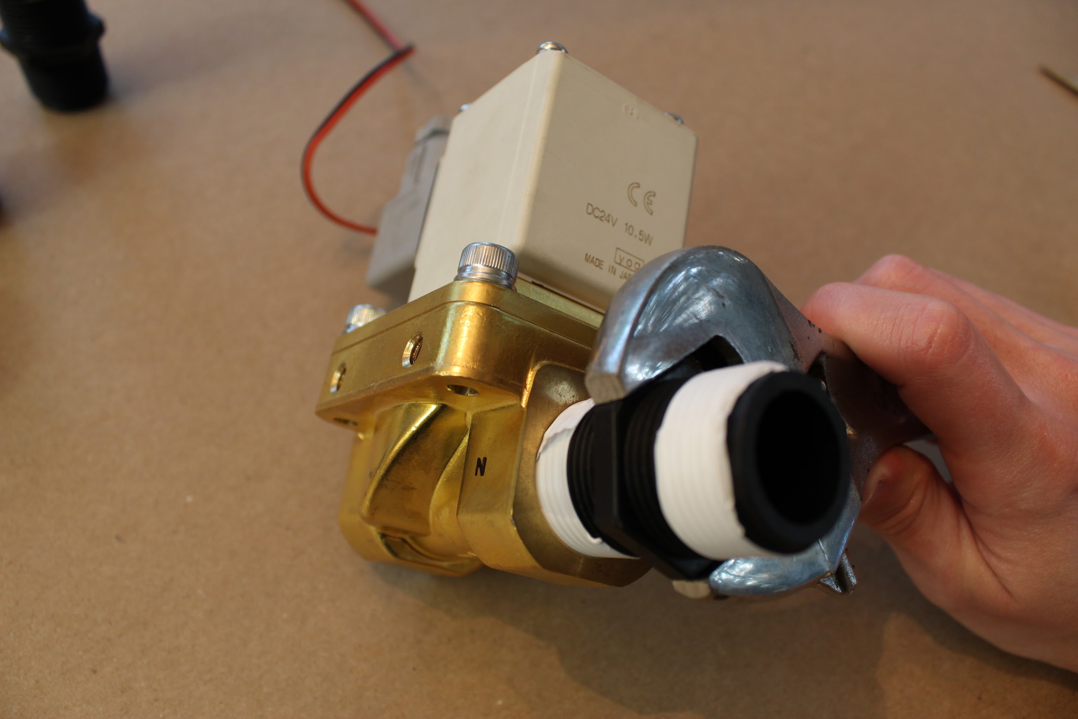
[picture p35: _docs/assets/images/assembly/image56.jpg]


**Step 3.** Ensure that the two side ports of the pressure regulator are
blocked off, with the plugs included with the part (and Teflon tape, as
always). Attach a ¼" NPT push-to-connect adapter to the pressure
regulator on the "outlet" side: check the bottom of the part to
determine which side is "IN" for "inlet". The inlet manifold will have
two ¼" NPT ports on the same side: plug one of those with the manifold
plug, and attach the other end to the ¼" NPT connector. Attach the other
end of this connector to the "inlet" end of the pressure regulator.

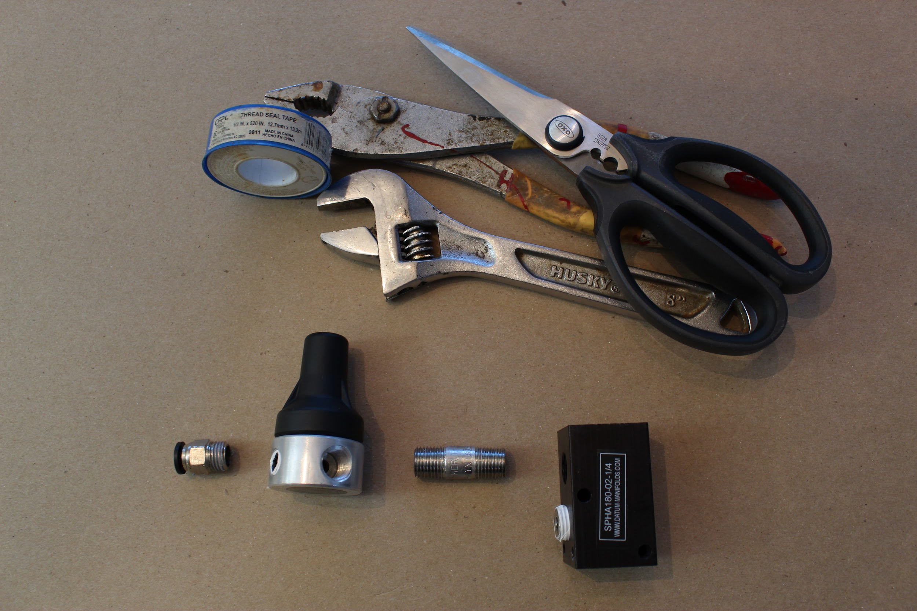
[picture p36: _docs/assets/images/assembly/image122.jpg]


**Step 4.** **Mounting the inlet manifold.**

First, attach the 3D-printed "Inlet manifold bracket", by pushing two
standard button-head screws down from the top of the piece (as shown,
such that the button heads fall in the grooves), then loosely attaching
a hex nut to each. Then, slide the two hex nuts into a T-slot of a short
(5 ⅞") 80/20 piece, and use an Allen key to secure the screws such that
the printed piece is as far to the "right" as it can go (as shown),
without the hex nuts extended past the length of 80/20.

Tip: when attaching hex nuts, make sure the side with the nub is facing
down (such that it touches the inner channel of the 80/20 T-slot).

Then, insert the inlet manifold into the printed piece, as shown: if the
printed part is to the right of the 80/20 length, then the pressure
regulator should be oriented away from you. Insert the 2" button head
hex drive screws through the remaining holes in the 3D printed piece, to
secure the inlet manifold, as shown (also away from you). Finally,
attach a washer (W_10_NARROW_0.406OD_316_SS) and hex nut
(LN_10-32_STAINLESS_18-8) to each.

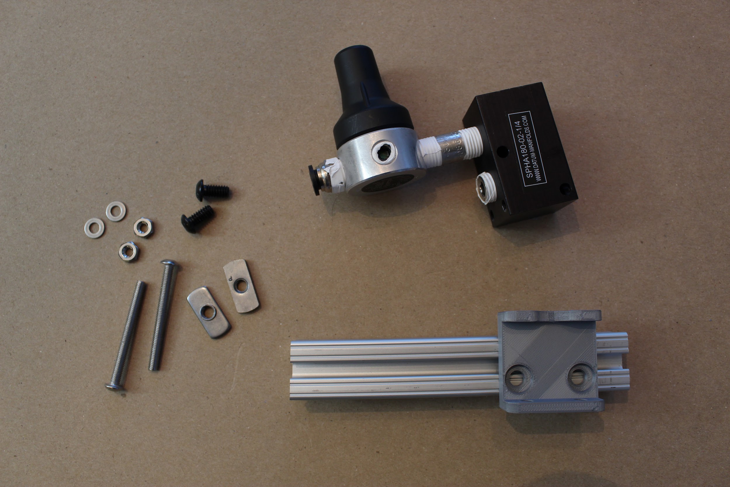
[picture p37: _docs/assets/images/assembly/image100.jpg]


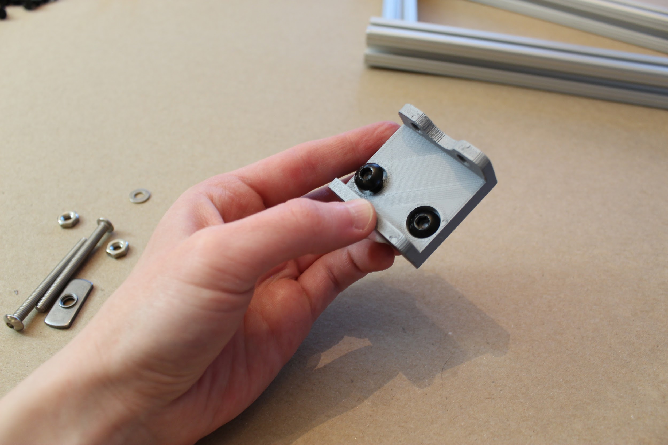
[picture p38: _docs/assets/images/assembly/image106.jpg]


**Step 5. Attach the "Expiratory outlet bracket to PEEP".**

Drop one standard button head hex screw down the deeper channel, and
attach as before: loosely screw on a hex nut, slide it in the channel,
and then use an Allen key to tighten the screw. This time, tighten the
hex screw such that the printed part is in-line with the edge of the
80/20 piece, as shown. Then, insert a second button head hex screw,
facing outward as shown, and loosely attach a hex nut (you will tighten
this later).

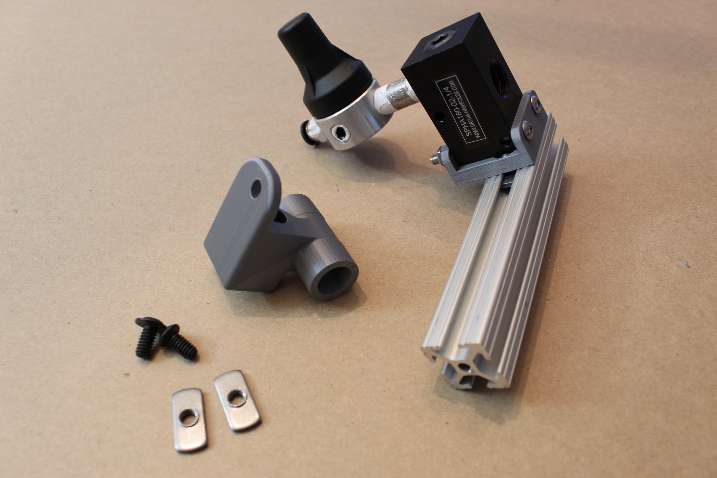
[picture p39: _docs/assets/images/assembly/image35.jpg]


**Step 6. Attach corner brackets to finish this frame piece.**

Pre-assemble the gusset (corner) brackets by inserting a hex screw into
each hole, and then loosely attaching a hex nut to each, as shown.
Tighten the gussets so that they align with the edge of the 80/20 piece,
as shown, keeping the second hex nut on each piece loose. (You will use
these to attach another 80/20 piece later.)

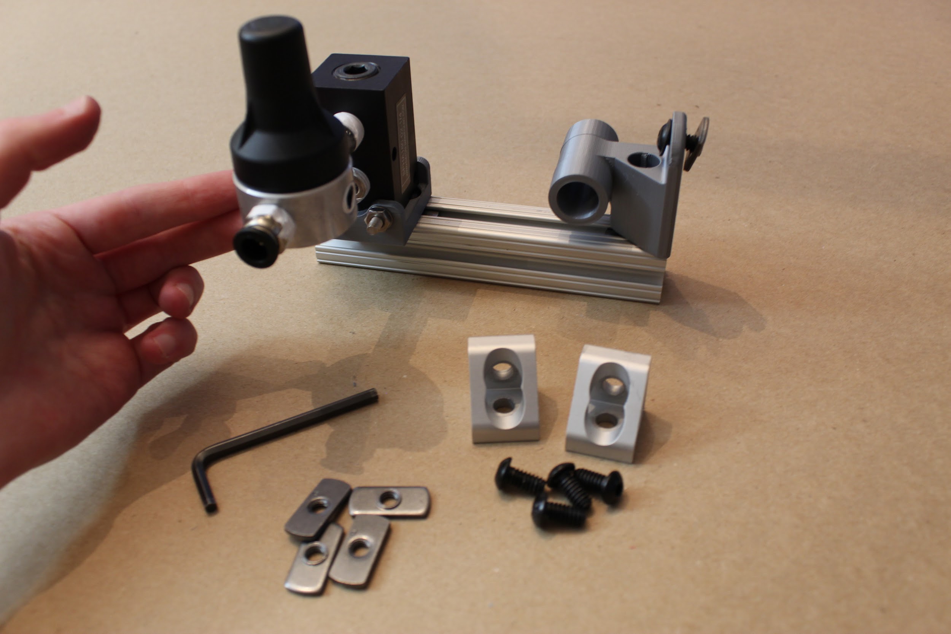
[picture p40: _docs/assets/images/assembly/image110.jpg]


**Step 7. Attach cable tie and side panel screw.**

If you intend to use the cable P-clip for cable management, and to
attach the HPDE side panels, attach the P-clip using a standard button
head hex screw, and mount an additional hex screw for attaching the side
panel later.

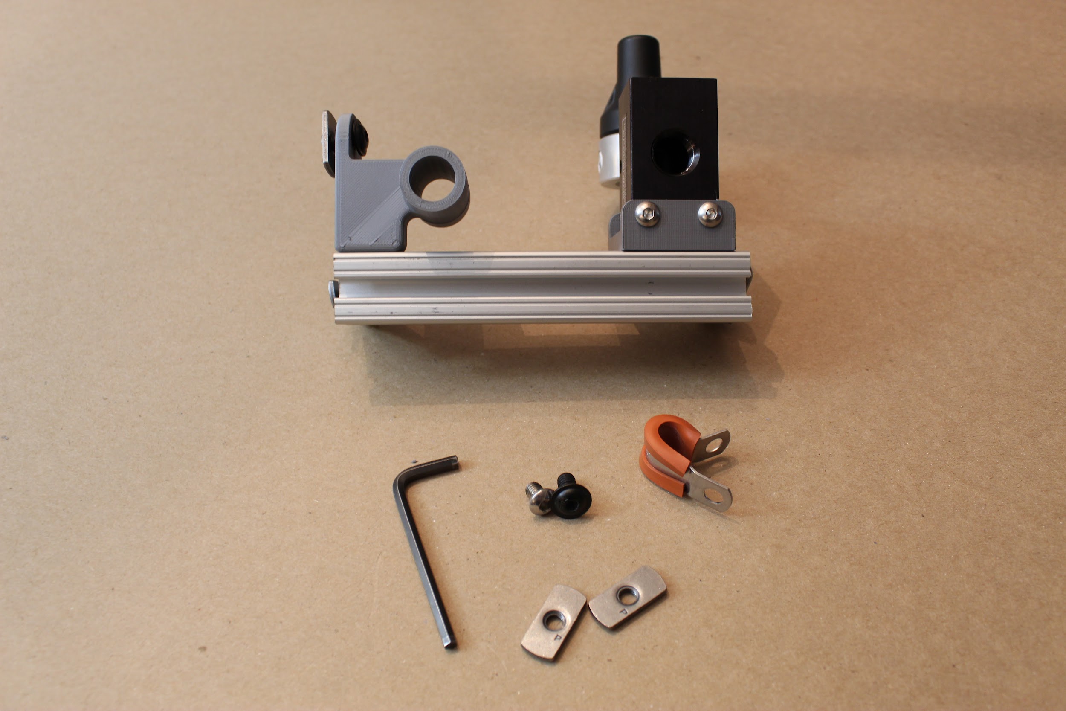
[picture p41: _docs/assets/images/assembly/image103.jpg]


Progress: One piece of the bottom frame is assembled!

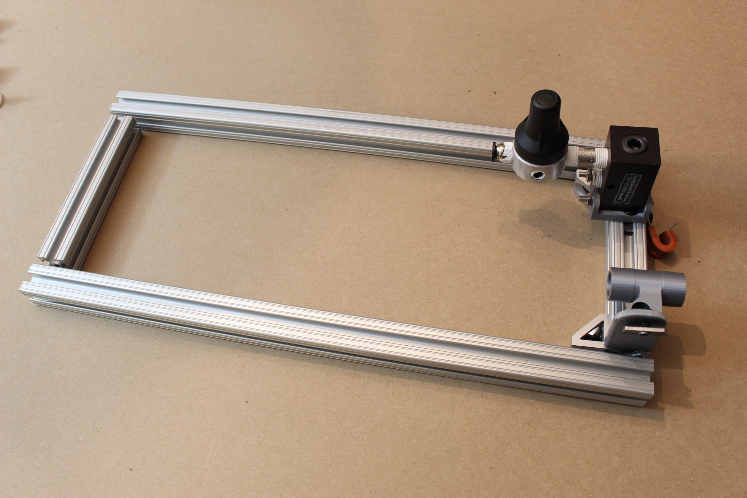
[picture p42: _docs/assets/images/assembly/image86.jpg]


**Step 8. Assemble the opposite side of the frame.**

Assemble a second short (5 ⅞") piece of 80/20 as shown: this uses the 3D
printed part called the "Expiratory DAR filter bracket", which will
mirror the "Expiratory outlet bracket to PEEP" part on the opposing
frame leg. Also, attach three gusset (corner) brackets, as shown.

```{admonition} Note:
if you intend to attach the side panels, leave off the
corner bracket on the same side as the 3D printed piece. If you're not
using the side panels, keep the bracket here for additional support!
```

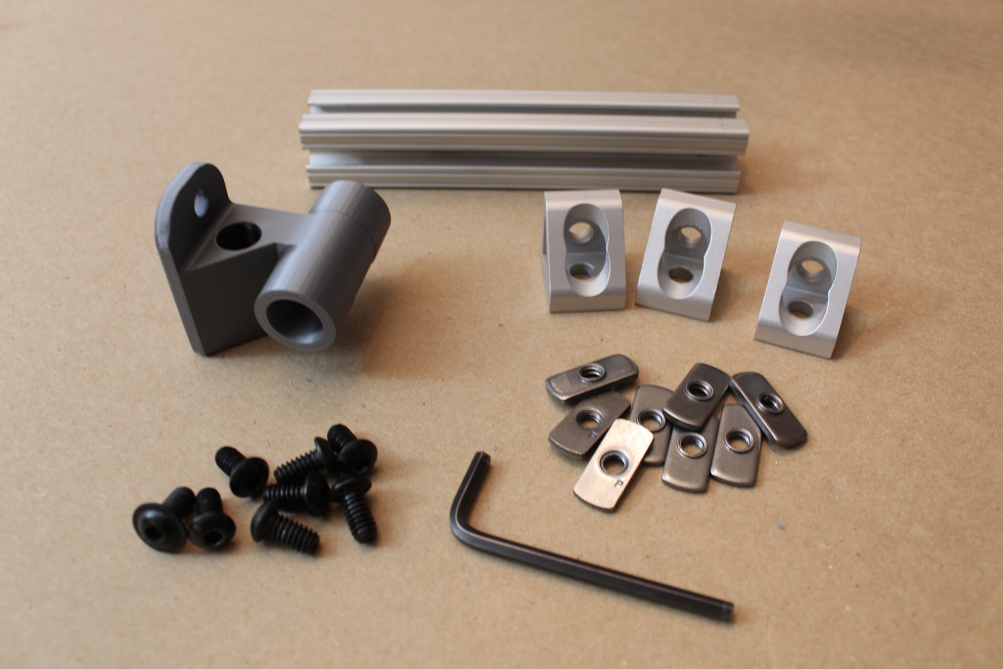
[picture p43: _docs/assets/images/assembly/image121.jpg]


**Step 9. Attach side panel screws.**

As before, if you plan to attach HDPE side panels later on, attach the
screws for them now, as shown.

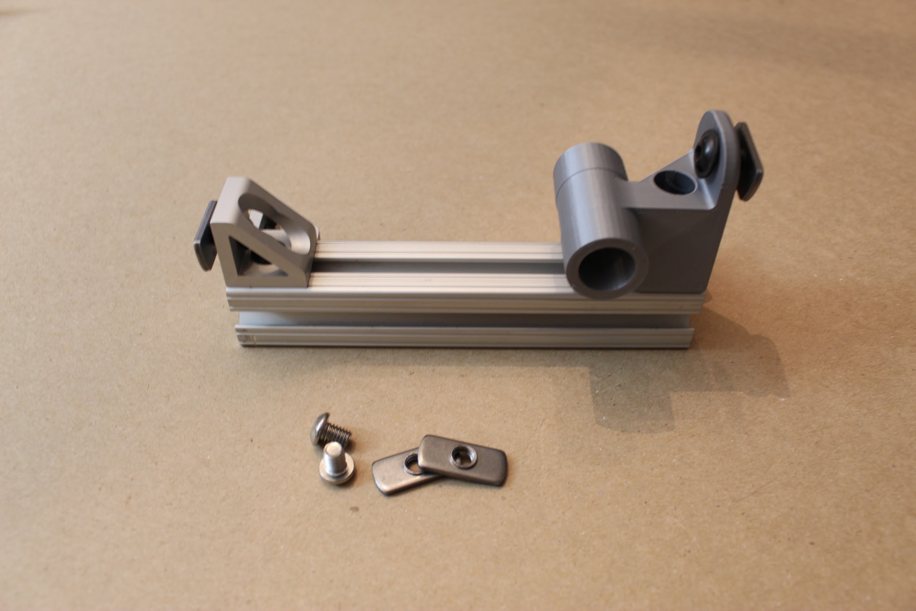
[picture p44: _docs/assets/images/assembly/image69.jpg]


**Step 10. Attach the expiratory solenoid assembly to the frame.**

-   First, assemble and attach two gusset (corner) brackets to their hex
    > screws/nuts, then affix to a long (17 ⅞") leg of the framing,
    > leaving 1" from the end of the piece on each side (that is,
    > leaving space for a vertical piece of 80/20).

-   Then, attach three hex screws/nuts to the lower rows of each
    > 90-degree angle bracket as shown; then attach the angle brackets
    > by inserting a short (1mm long) button head screw through the
    > topmost hole of each angle bracket in the opposite direction.
    > These shorter hex screws will screw directly into the solenoid.

-   Finally, slide the hex nuts attached to the angle brackets into the
    > T-slot of the 80/20 piece, such that the gusset brackets and
    > solenoid are oriented above the 80/20 piece, as shown. Loosely
    > tighten these in place; you will adjust the position of the
    > solenoid later.

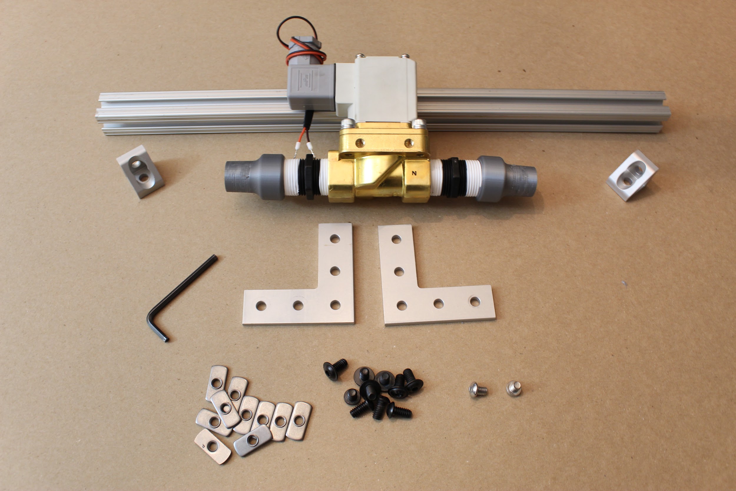
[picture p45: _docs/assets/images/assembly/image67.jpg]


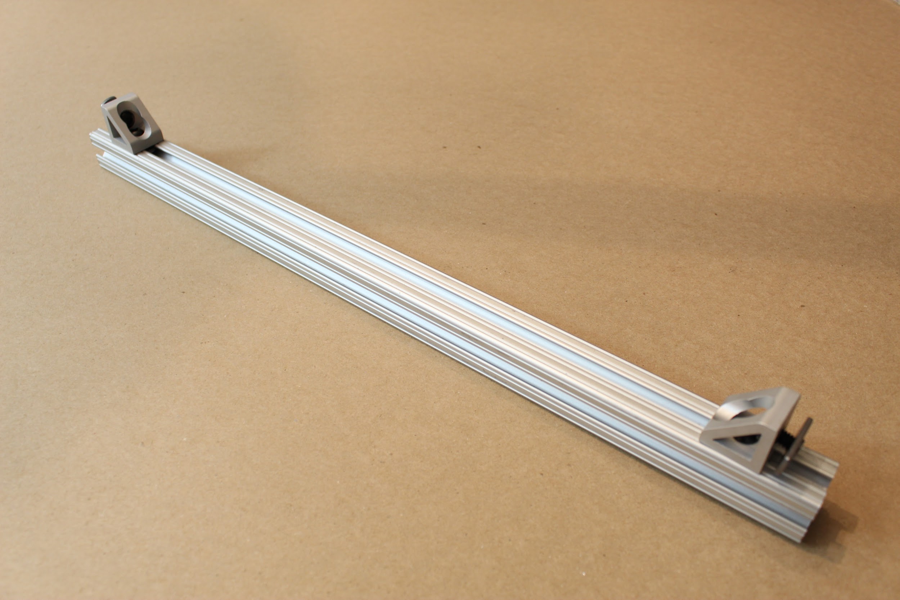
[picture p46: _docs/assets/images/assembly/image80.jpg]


**Step 11. Attach gusset (corner) brackets to the opposing 80/20 leg.**

Assemble the gusset (corner) brackets with hex screw/nuts as before, and
attach them to a long (17 ⅞") 80/20 piece. Leave 1" of space from each
of the side gussets (sufficient space for a vertical 80/20 piece), and
affix the third bracket just off-center (to support a centered, vertical
80/20 piece).

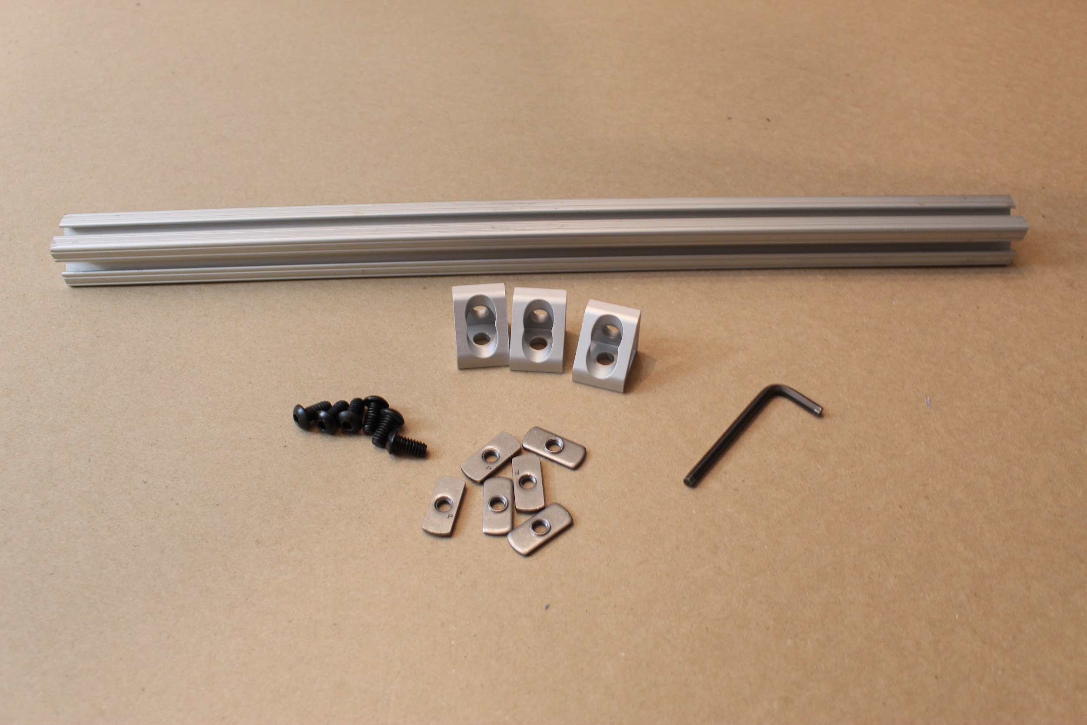
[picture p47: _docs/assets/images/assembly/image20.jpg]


**Step 12. Assemble the bottom frame components.**

Slide the hex nuts on the shorter 80/20 pieces you have assembled into
the longer 80/20 slots, and use an Allen key to tighten the screws in
place, as shown. The shorter 80/20 legs should be flush with the ends of
the longer 80/20 legs when you are done, and the gusset (corner)
brackets will help stabilize the frame.

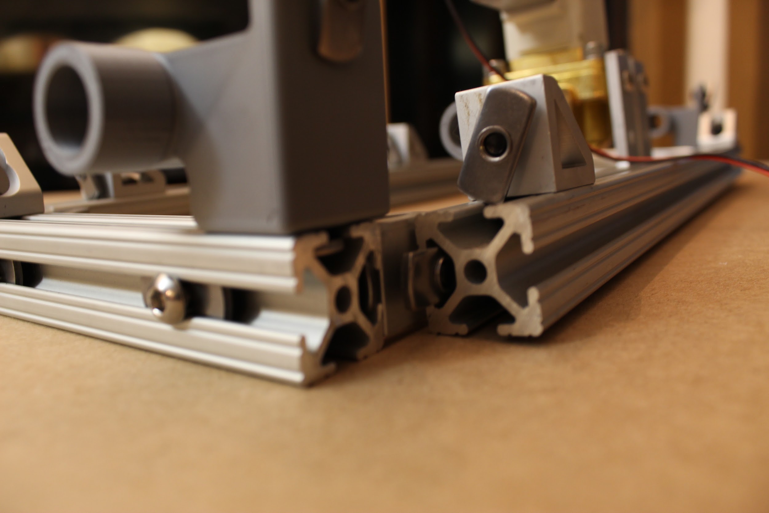
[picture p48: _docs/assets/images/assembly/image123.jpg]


**Step 13. Attaching the ventilator "feet" and bottom panel.**

If you are attaching the lower, perforated HPDE sheet, insert the rubber
grommet. Pre-assemble the shorter (1mm) button head screws to hex nuts,
and the leveling mounts (feet) to hex nuts. Use these to attach the
lower HPDE panel as shown, by sliding the hex nuts along the long
channels on the bottom of the frame assembly; then tighten in place.

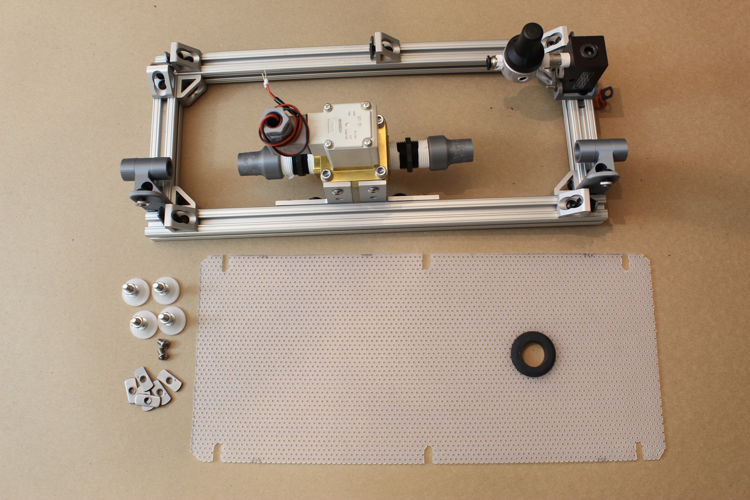
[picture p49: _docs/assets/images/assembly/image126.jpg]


**Step 14. Attach the respiratory tube segment.**

Awesome- almost done with the lower level of the ventilator! As a last
step, attach the short segment of respiratory circuit between the
"Expiratory outlet bracket to PEEP" and the nearest "22mm to .75NPTM
adapter". You'll be able to twist this on by hand.

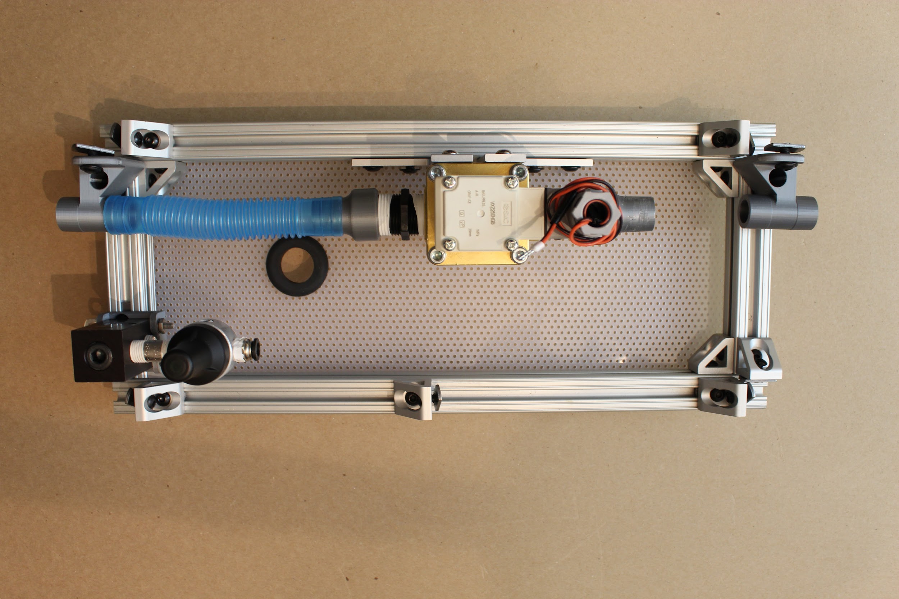
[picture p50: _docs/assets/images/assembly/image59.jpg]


### 2.2 Assembling the frame sides

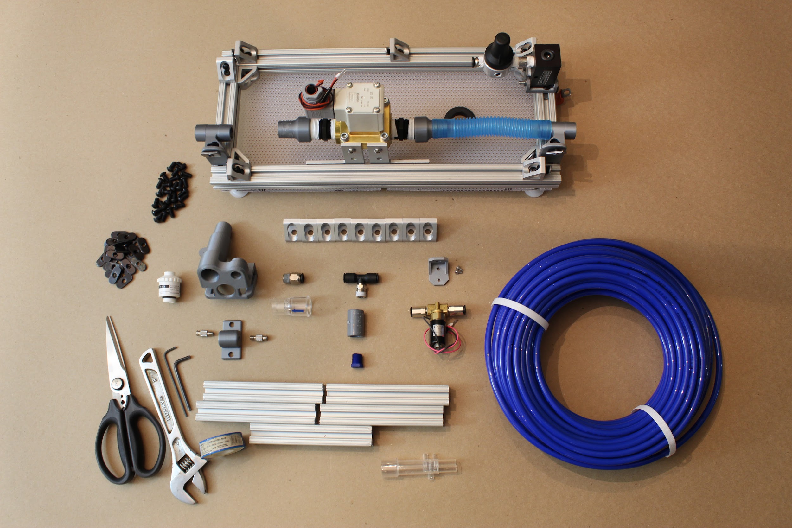
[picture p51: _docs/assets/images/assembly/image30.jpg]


**Step 1. Attach the proportional valve to its mount.**

Use the two socket head screws (6mm long) to attach the proportional
valve to the 3D printed "proportional valve bracket". The inlet should
be to the right in the orientation shown below.

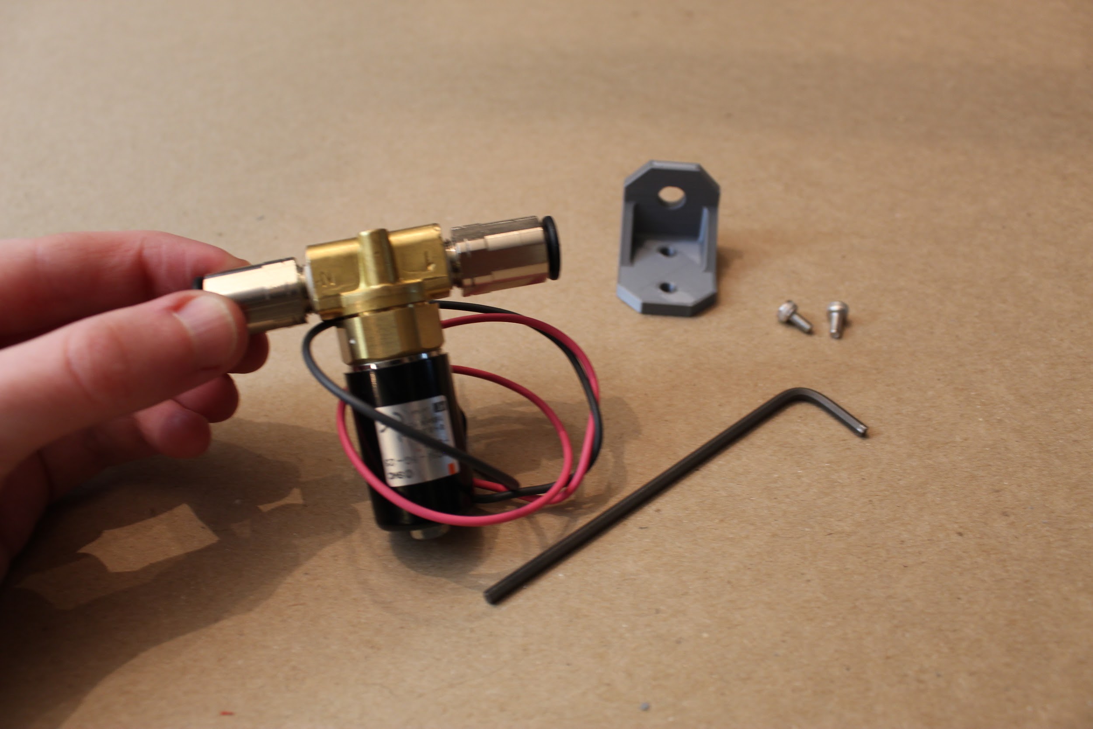
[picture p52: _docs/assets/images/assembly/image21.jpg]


**Step 2. Attach the pressure relief valve to its adapters.**

Assemble the T-line push-to-connect adapter, to a female-female ¼" NPT
connector, and finally to the Nylon pressure release valve.

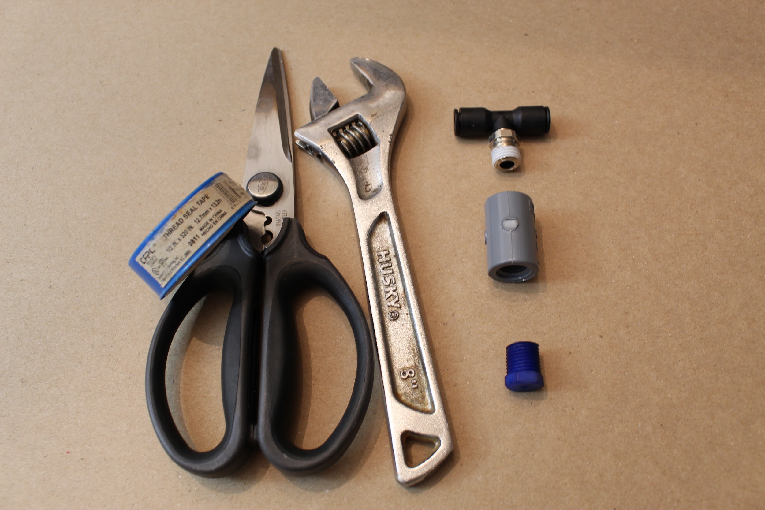
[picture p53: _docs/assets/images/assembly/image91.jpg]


**Step 3. Attach the luer lock connectors to the luer lock filter
mount.**

These pieces will screw in, with the luer lock portions facing outwards.

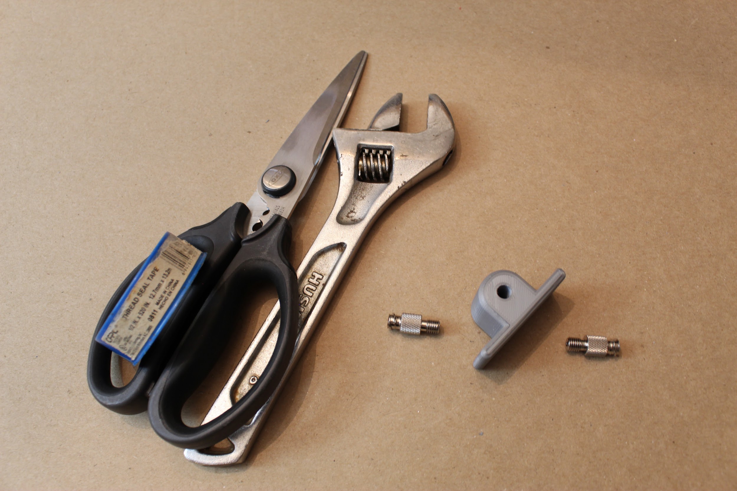
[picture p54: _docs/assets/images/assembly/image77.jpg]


**Step 4. Assemble the sensor atrium.**

Attach the ¼" NPT push-to-connect adapter, check valve, and oxygen
sensor into the appropriate holes in the "Sensor Atrium Manifold", as
shown. Do not push the check valve into the device too far, as it may
restrict air flow within the atrium.

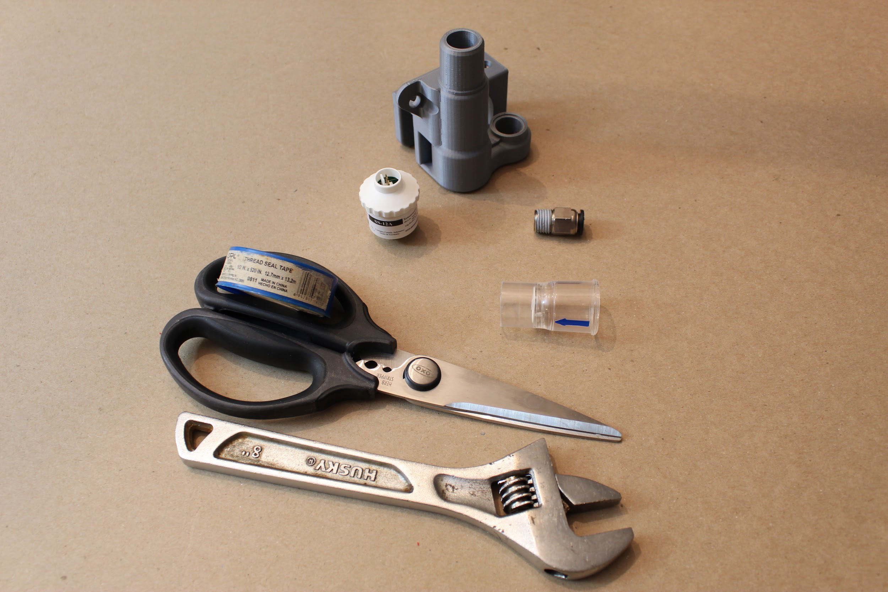
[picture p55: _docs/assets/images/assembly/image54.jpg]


**Step 5. Attach sensor atrium to a short 80/20, and then to the
device.**

Affix button head screws/nuts to the sensor atrium, with hex nuts facing
towards one another, as shown. Slide the hex nuts along T-slots on
either side of a short (5 ⅞") 80/20 piece; then insert this vertically
into the device as shown. Tighten into place via the hex screws on the
lower gusset (corner) brackets.

```{admonition} Note:
If you are attaching the side panels, be sure to use a SHORT
nut on the sensor atrium (the nut on the side with two, farther from the
oxygen sensor), and keep the short side facing down when inserting. This
will allow the sensor atrium to drop lower and align with the holes in
the front panel.
```

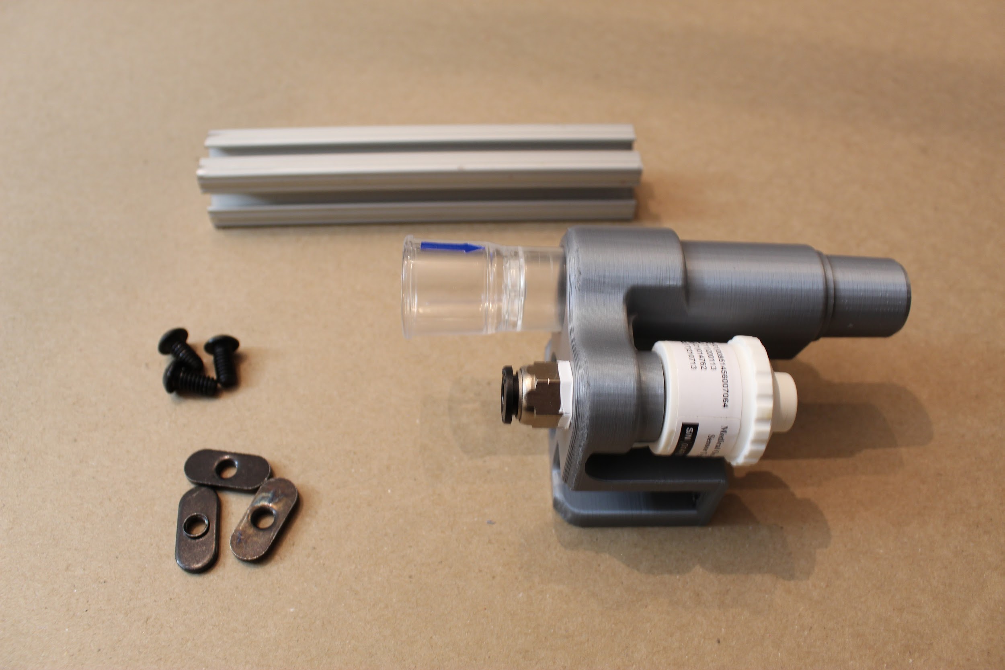
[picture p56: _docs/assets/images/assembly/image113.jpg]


**Step 6. Attach the second vertical leg, along the "Expiratory DAR
filter bracket".**

As before, slide a short (5 ⅞") 80/20 piece into the position shown,
then tighten the hex screws.

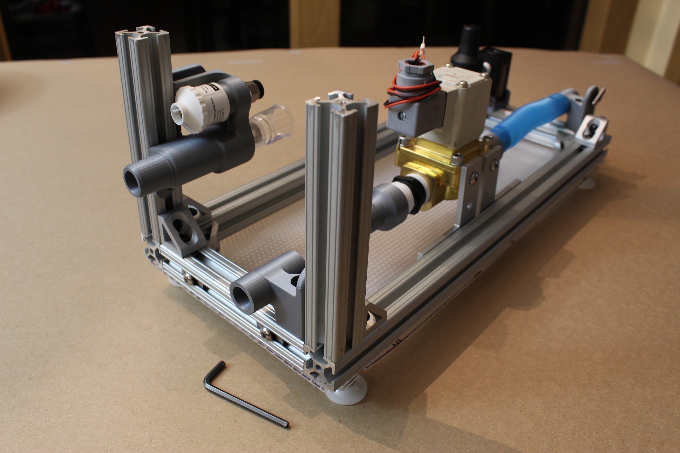
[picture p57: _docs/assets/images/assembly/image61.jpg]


**Step 7. Attach the luer lock filter bracket to the newly inserted
80/20 leg.\

```{admonition} Note:
If you're attaching the side panels, use another SHORT 80/20
nut in the uppermost spot on the bracket. We'll want this part to be as
high as possible to match up with the holes on the front panel.
```

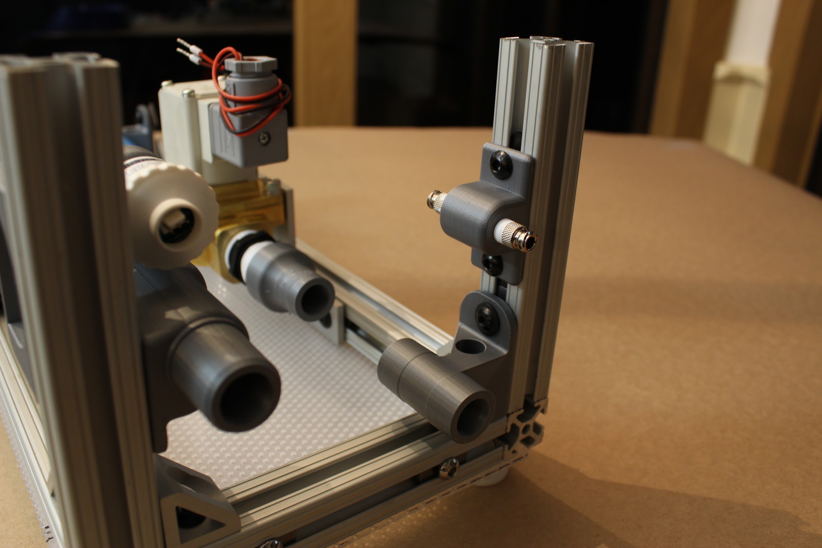
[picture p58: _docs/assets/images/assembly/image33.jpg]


**Step 8. Attach the third vertical 80/20 leg, then attach the
proportional valve mount.**

Insert a third, short (5 ⅞") 80/20 piece, then tighten the hex screw to
hold it in place. Use another standard hex screw/nut to attach the
proportional valve mount to this piece, towards the inside of the
device, such that the push-to-connects roughly align vertically with the
push-to-connect on the sensor atrium.

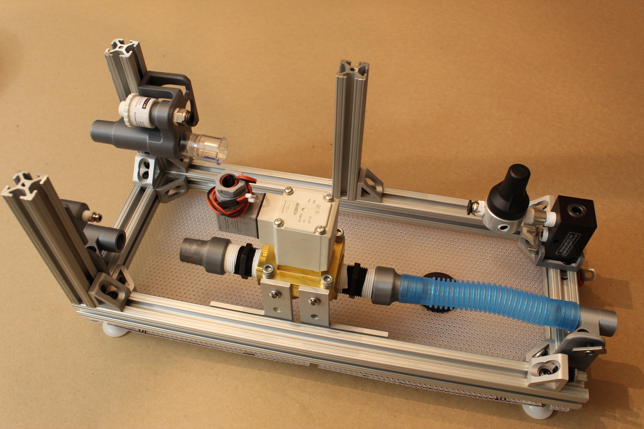
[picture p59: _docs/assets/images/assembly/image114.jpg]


**Step 9. Attach the final two vertical 80/20 pieces in the remaining
corners.**

```{admonition} Note:
If you're attaching the side panels, now is the time to
insert 80/20 nuts on the vertical 80/20 pieces as well as the long 80/20
pieces on the lower frame.
```

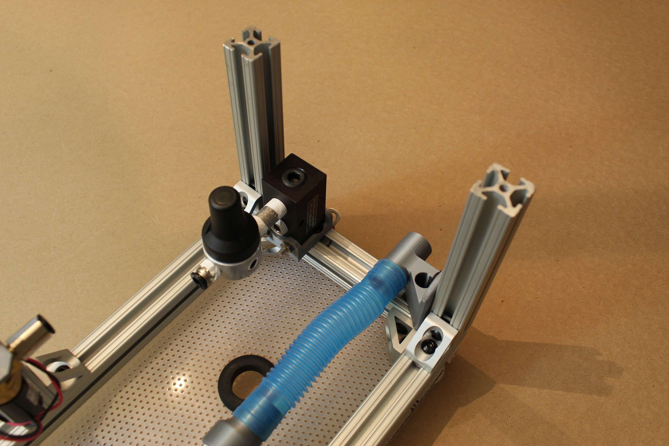
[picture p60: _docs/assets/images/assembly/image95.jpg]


**Step 10.** **Attach the D-Lite.**

Attach a blue silicone connector to the "Expiratory DAR filter bracket),
on the side within the device. Then, insert the D-Lite between the
silicone connector and the nearest "22mm to .75 NPTM adapter", adjusting
the position of the expiratory solenoid assembly until the D-lite is
firmly connected at each end. The smaller end of the D-lite should fit
within the "22mm to .75 NPTM adapter". Then, use an Allen key to tighten
the hex screws on the 90 degree angle brackets to maintain the position
of the solenoid.

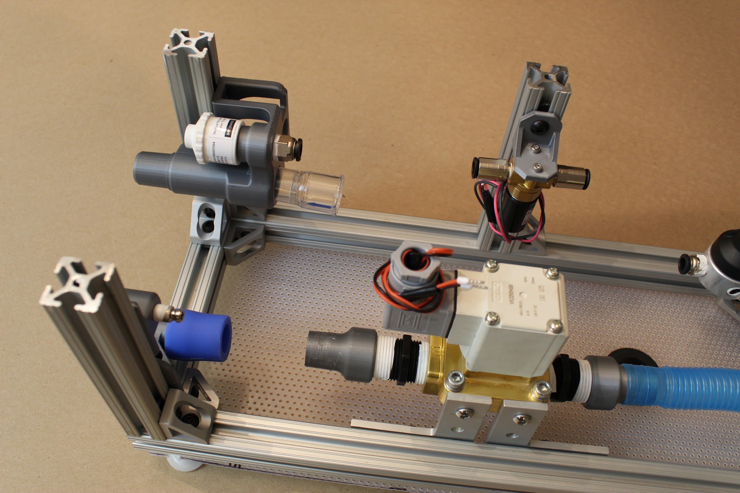
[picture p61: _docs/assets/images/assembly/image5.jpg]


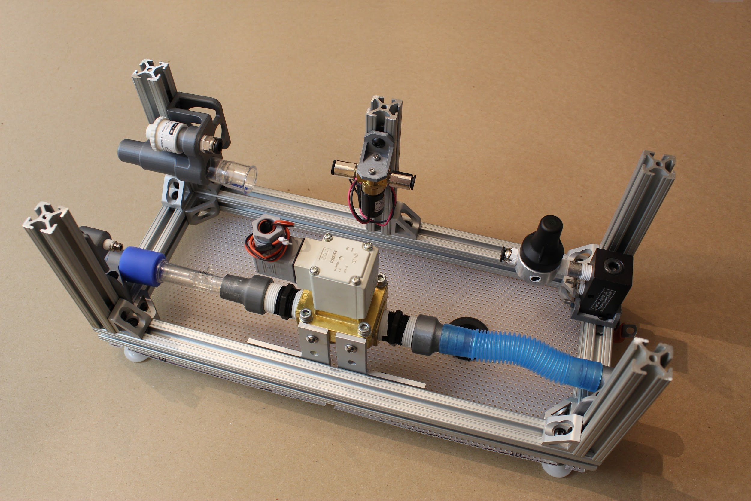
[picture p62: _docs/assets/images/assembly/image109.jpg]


**Step 11. Attach the pressure release valve and pneumatic tubing.**

Cut the pneumatic tubing into three segments: two of length 2.5"
(6.35cm), and one of length 5.5" (13.97cm). Insert the long piece
between the push-to-connect adapters attached to the pressure regulator
and proportional valve. Insert the two shorter tubes into either
push-to-connect on the pressure relief valve assembly; then attach these
between the sensor atrium and proportional valve push-to-connects, as
shown. These tubing lengths should keep the proportional valve fairly
centered.



### 2.2 Assembling the frame top



**Step 1. Attach the lifting handles.**

Use the lifting handle screws (SHCS_0.25-20x0.75_Gr8_ASTM_F1136), with
standard hex nuts, to mount the lifting handles to two short (5 ⅞")
pieces of 80/20, such that the handles are centered on the pieces.



**Step 2. Prepare all the remaining gusset (corner) brackets.**

Attach the hex screws/nuts loosely to the 13 remaining gusset (corner)
brackets, so that they can be attached readily in future steps.



**Step 3. Attach gusset (corner) brackets, as shown.**



**Step 4. Cut and punch DIN rail pieces.**

Cut the DIN rail to 7 ⅞" (20.0025cm) lengths, punching or drilling holes
½" (1.27cm) from each edge large enough to support the standard button
head hex screws.



**Step 5. Attach the DIN rails and assemble the rest of the top level.**

-   Slide two long (17 ⅞") 80/20 pieces onto one of the shorter pieces,
    > and screw in place. Add an additional gusset (corner) bracket to
    > each long leg, as shown, leaving 1" of space from the end (to
    > support a vertical piece).

-   Use a short (1mm) button head hex screw, a zinc washer
    > (W_0.25_FLAT_THICK_GR8_YELLOW_ZINC), and a standard hex nut to
    > attach each end of the DIN rails to the frame, as shown. Slide an
    > additional gusset (corner) bracket between the rails on one side-
    > this will support the central vertical channel on the device.

-   Once the DIN rails are roughly in place (exact positions can be
    > adjusted later), use the remaining gusset (corner) brackets and
    > assembled short 80/20 piece, and mirror the other side of the
    > assembly, as shown.



**Step 6. Finally, slide the top frame directly into the vertical 80/20
channels of the device, and tighten all hex screws.**



Congrats! The basic hardware assembly is complete!

## Part 3. Electronics Assembly

### 3.1 Assembling the Sensor Board

\[Image of all components laid out in order/piles, with labels\]





You will also need:

-   A soldering iron

-   Solder

-   Helping hands for holding parts while soldering

-   Wire cutters (for clipping off long capacitor/resistor legs)

**Step 1. Solder the 40-pin stackable RPi header to the Actuator PCB.**

Push the pins up from the bottom of the board, as shown, and then solder
into place.



**Step 2. Solder the 4-pin, 3-pin, and 2-pin 0.1" headers onto the board
(positions J2, J3, J4).**

Break the pins off the larger header array in units of 4, 2, and 3 using
pliers. Insert the short end of the pins into the holes from the top of
the board, and solder from below. This will leave the long ends of the
pins sticking up vertically from the board, as shown:



**Step 3. Solder the 330 Ohm resistor onto the board (position R1).**

Bend the resistor legs before inserting into the board from above.
Ideally, solder the resistor in place such that the resistor is hovering
just above the board. Then, snip the long legs off from the back of the
board (cutting above the tiny "cone" formed by the solder) using wire
cutters.



**Step 4. Solder the two 10 µF, 25V capacitors onto the board (positions
C1, C2).**

Insert the capacitors from the top of the board until the legs snap into
place. Be sure that the longer capacitor leg is inserted into the hole
corresponding to the "+" sign. After soldering, snip the long legs off
from the back of the board using wire cutters.



**Step 5. Solder the TL7660 (the rail splitter for the INA126) onto the
board (position U1).**

Be sure to orient the small circle on the top of the part to the
indicated notch drawn on the board.



**Step 6. Solder the INA126 (the instrumentation amplifier for the
oxygen sensor) onto the board (position U2).**

As before, make sure that the notch on the part aligns with the notch
drawn on the PCB.



**Step 7. Solder the Amphenol 5 INCH-D2-P4V-MINI (differential pressure
sensor) onto the board (position U3).**

Bend all four pins evenly and orient the part such that the black ports
face towards the outside of the board. The pressure lines will attach
here.



**Step 8. Solder the Adafruit ADS1115 (12-bit ADC) to the board.**

First, solder the pins to the ADC itself, with the long ends facing
down. Then insert the pins through the board and solder from the back
side.





**Step 9. Finally, solder the Amphenol 1 PSI-D-4V-MINI (airway pressure
sensor) to the board.**

As before, bend all four pins together, then insert and solder from the
back side of the board. Be sure the ports are facing out: we will attach
pressure lines here as well.



### 3.2 Assembling the Actuator Board

\[Image of all components laid out in order/piles, with labels\]





You will also need:

-   A soldering iron

-   Solder

-   Helping hands for holding parts while soldering

-   Wire cutters (for clipping off long capacitor legs)

**Step 1. Solder the 40-pin stackable RPi header to the Actuator PCB.**

Push the pins up from the bottom of the board, as shown, and then solder
into place.





**Step 2. Solder the 2-pin 0.1" header onto the board (position J5).**

Insert the short end of the pins into the holes from the top of the
board, and solder from below. This will leave the long ends of the pins
sticking up vertically from the board, as shown:



**Step 3. Solder the 100 µF, 16V capacitor onto the board (position
C1).**

Insert the legs of the capacitor into the slots from the top of the
board. The longer leg should be inserted into the side marked "+". Once
the capacitor is soldered in place, use wire cutters to clip off the
long legs from the back.



**Step 4. Solder the ULN2003A (Darlington array) into place (position
U1).**

Be sure to match the notched end of the part to the notch indicated on
the board.



**Step 5. Solder the two 6.8 µF, 50V capacitors onto the board
(positions C2, C3).**

As before, ensure that the longer capacitor legs are inserted through
the side marked with the "+". Once the parts are soldered in, snip the
long legs from the back of the board.



**Step 6. Solder the 24-to-5 V DC-DC converter (CUI PDQ15-Q24-S5-D) onto
the board, as shown.**



**Step 7. Solder the 3 2-pin screw terminals (5.08mm pitch) to the
board, as shown.**

Be sure to orient all three such that wires can be screwed into the
terminals from the outside of the board (as shown).





**Step 8. Finally, jumper the 2-pin header.**

You can use a pin jumper ("shunt") if you have one, or crush the pins
together with a pair of pliers, and then solder the two pins together.
We display the latter method, below:



**Step 9. The actuator board is ready to go!**



### 3.3 Assembling the PCB-RPi stack



**Step 1. Attach three gas sampling lines to the port on the two
pressure sensors.**

The differential pressure sensor has two ports. If you have an
airway-safe glue, feel free to glue these in place (not required).



**Step 2. Begin stacking the board by attaching the DIN rail mounts.**

You can pre-"tap" the 3D printed DIN rail mounts using the small screws
that come with the Raspberry Pi. Then, screw four of the 16mm standoffs
through the Raspberry Pi from above, and into the DIN rail mounts, as
shown.



**Step 3. Next, add the sensor board.**

Connect the sensor board via the stackable headers, then use another
four 16mm standoffs to attach the board by screwing these into the
original four standoffs, using pliers as needed.



**Step 4. Add the actuator board.**

Connect the actuator board via the stackable headers, then use the four
screws that came with your Raspberry Pi to attach the board, as shown.



## Part 4. Putting it all together

### 4.1 Wrapping it up.



**(Optional step:** Attach the side panels using the shorter 80/20 hex
screws, as you go.)

**Step 1. Attach the DAR filters.**

Insert these by hand to the appropriate ports on the front of the
device, as shown: these will attach to the sensor atrium and the
expiratory DAR filter bracket. The DAR filters indicate which end should
face the patient.



**Step 2. Attach the luer lock filter.**

This can be twisted on by hand to the luer lock adapter at the front of
the device.



**Step 3. Attach the PEEP valve.**

If you're using a commercial PEEP valve, begin by attaching the blue
silicone connector. Then, insert the PEEP valve into the 3D printed
"22mm to commercial PEEP adapter"- then plug this assembly into the
silicone connector.



**Step 4. Attach the power supply.**

Pull the tab on the Meanwell power supply to attach it to the DIN rail
closest to the back of the device. It may be necessary to adjust the
position of this DIN rail to ensure that the power supply is not
touching the expiratory solenoid or inlet manifold/pressure regulator.
Feel free to reposition as needed!

```{admonition} Note:
if you wish to attach a rear HPDE panel, we recommend
inserting the power cable to the power supply through the grommet of the
rear panel before insertion of the power supply into the device. Do this
now! You can also attach the "Rear Panel Vent"s to the rear panel; they
will snap right in.
```



**Step 5. Attach the luer lock plug to the D-Lite.**

The third port on the D-Lite (physically removed from the other two) is
not needed; plug that now with a luer lock plug.



**Step 6. Attach the power and ground wires to the PCB stack. Then wire
the proportional valve and solenoid.**

Use a small flathead screwdriver to attach the power and ground from the
power supply to the PCB stack where indicated. Then do the same for the
proportional valve wires and the expiratory solenoid wires: the board
indicates which pair goes where!



**Step 7. Attach the gas sampling lines to the D-Lite.**

Use the luer lock connector on the smaller of the two ports, then
connect the two gas sampling lines from the differential pressure sensor
(from the same sensor on the Sensor Board).



**Step 8. Attach the gas sampling line to the luer lock filter mount
adapter.**

The third gas sampling line runs from the second pressure sensor; attach
this to the inner luer lock adapter on the luer lock filter mount.



**Step 9. Plug in any required cables to connect the monitor and
keyboard.**

Run the cables outside of the box through the rubber grommets; wire ties
can assist with cable management.

**Congratulations! You're done!**



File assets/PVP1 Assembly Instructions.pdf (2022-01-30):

### PVP1 Assembly Instructions

This guide should help you assemble the ventilator from the parts found in the Bill of Materials: https://www.peoplesvent.org/en/latest/bom.html
We’ll first show you how to assemble the hardware, then the electronics, and finally put the two together.

### Part 1. 3D Printed Components and Enclosure

1.1 3D Printing Adapters and Brackets.

Before we can get started with assembly, you’ll need to print a few parts using a standard 3D printer. (We ran our test prints on Prusa, MakerBot, FlashForge, and Creality3D printers.)

You can download all the STL files here for printing: https://www.peoplesvent.org/en/latest/assembly.html#d-printed-parts

Be sure to print airway components at as close to 100% infill as possible, and be mindful of printing orientation. An example printing setup is shown below. We do not recommend using supports or rafts unless you find them to be necessary, as they are challenging to remove. If there is a cylindrical channel, try to orient it vertically (such that the circle is traced along the build plate), which will improve circularity of the channel.


If you are using a Prusa i3, we also provide this print setup here.

### 1.2 Tapping the 3D Printed Components

Several of the 3D printed parts will need to be tapped to enable connection with other parts in the device- such as push-to-connect adapters. You will be able to tap all of these parts by hand (since the plastic cuts easily), and the Bill of Material contains the list of taps you will need, including specialized taps such as the M16:
https://www.peoplesvent.org/en/latest/bom.html

All required taps are shown below:

First, we will tap the Sensor Atrium component, which houses the oxygen sensor and “emergency breathing valve” check valve, and passes air from the inspiratory limb to the respiratory circuit (with a DAR filter in between).

Step 1. Use a ¼” NPT tap to thread the hole as shown below (the smaller airway hole on the flat side of the Sensor Atrium), where a push-to-connect adapter will attach.

Step 2. Use the M16 tap to thread the hole on the opposite side of the Sensor Atrium, where the oxygen sensor will attach.

Next, we will tap the adapters at either side of the expiratory solenoid.

Step 3. Use the ¾” NPT tap to thread the holes on the larger end of the two “22mm to 0.75 NPTM adapter” parts.


Last, we will tap the adapter to the pressure sampling lines.

Step 4. Finally, use the ¼”-28 tap to thread the two airway holes on the “Luer lock filter mount” part. These will hold the metal luer lock adapters to the gas sampling lines for monitoring pressure.

1.3 Cutting Enclosure Pieces.

Step 1. Laser cut, or cut out by hand, the six HPDE side panels.
Cut all panels out of the 1/16” HPDE sheets. If you wish to cut these pieces using a laser cutter, we provide DXF files here, under “Enclosure”: https://www.peoplesvent.org/en/latest/assembly.html
Cuts can also be made by hand using a sharp pair of scissors and a razor-cutter. Pieces are 17 ⅞” by 7 ⅞” (45.4025 cm by 20.0025 cm), or 7 ⅞” by 7 ⅞” (20.0025 cm by 20.0025 cm) along the outer dimensions. Inner hole placement can be determined from the documentation, also at: https://www.peoplesvent.org/en/latest/assembly.html
(We cut our side panels for the demo out of acrylic for ease of visibility.)


Step 2. Insert the rubber grommet(s).
The bottom panel includes a hole for a large rubber grommet. Insert this by hand. If you wish, you may also insert a small custom grommet in the back panel.

### Part 2. Basic Hardware Assembly

### 2.1 Assembling the bottom frame

Step 1. Cut the 80/20 (“T-slotted framing”) to appropriately sized pieces: In total, you will need 4 pieces of length 17 ⅞ in (45.4025 cm), and 9 pieces of length 5 ⅞ in (14.9225 cm).

You can cut the aluminum 80/20 pieces by hand with a hack-saw, or using machinery such as a bandsaw. Either way, be sure to file down any rough edges afterward!

Step 2. Attach the ¾” NPT (male-male) connectors to either side of the expiratory solenoid, and then attach the two “22mm to .75 NPTM adapter” parts to those, as shown. When attaching any airway threaded parts in this assembly process, be sure to use PTFE thread sealant tape, wrapping twice around the threads, in the direction shown (away from your body if the threads are oriented towards the right).
(Note: From now on, we will not explicitly write out the need for Teflon tape; be sure to use it whenever a threaded airway component is involved!)


Step 3. Ensure that the two side ports of the pressure regulator are blocked off, with the plugs included with the part (and Teflon tape, as always). Attach a ¼” NPT push-to-connect adapter to the pressure regulator on the “outlet” side: check the bottom of the part to determine which side is “IN” for “inlet”. The inlet manifold will have two ¼” NPT ports on the same side: plug one of those with the manifold plug, and attach the other end to the ¼” NPT connector. Attach the other end of this connector to the “inlet” end of the pressure regulator.

Step 4. Mounting the inlet manifold.
First, attach the 3D-printed “Inlet manifold bracket”, by pushing two standard button-head screws down from the top of the piece (as shown, such that the button heads fall in the grooves), then loosely attaching a hex nut to each. Then, slide the two hex nuts into a T-slot of a short (5 ⅞”) 80/20 piece, and use an Allen key to secure the screws such that the printed piece is as far to the “right” as it can go (as shown), without the hex nuts extended past the length of 80/20.
Tip: when attaching hex nuts, make sure the side with the nub is facing down (such that it touches the inner channel of the 80/20 T-slot).

Then, insert the inlet manifold into the printed piece, as shown: if the printed part is to the right of the 80/20 length, then the pressure regulator should be oriented away from you. Insert the 2” button head hex drive screws through the remaining holes in the 3D printed piece, to secure the inlet manifold, as shown (also away from you). Finally, attach a washer (W_10_NARROW_0.406OD_316_SS) and hex nut (LN_10-32_STAINLESS_18-8) to each.


Step 5. Attach the “Expiratory outlet bracket to PEEP”.
Drop one standard button head hex screw down the deeper channel, and attach as before: loosely screw on a hex nut, slide it in the channel, and then use an Allen key to tighten the screw. This time, tighten the hex screw such that the printed part is in-line with the edge of the 80/20 piece, as shown. Then, insert a second button head hex screw, facing outward as shown, and loosely attach a hex nut (you will tighten this later).

Step 6. Attach corner brackets to finish this frame piece.
Pre-assemble the gusset (corner) brackets by inserting a hex screw into each hole, and then loosely attaching a hex nut to each, as shown. Tighten the gussets so that they align with the edge of the 80/20 piece, as shown, keeping the second hex nut on each piece loose. (You will use these to attach another 80/20 piece later.)


Step 7. Attach cable tie and side panel screw.
If you intend to use the cable P-clip for cable management, and to attach the HPDE side panels, attach the P-clip using a standard button head hex screw, and mount an additional hex screw for attaching the side panel later.

Progress: One piece of the bottom frame is assembled!


Step 8. Assemble the opposite side of the frame.
Assemble a second short (5 ⅞”) piece of 80/20 as shown: this uses the 3D printed part called the “Expiratory DAR filter bracket”, which will mirror the “Expiratory outlet bracket to PEEP” part on the opposing frame leg. Also, attach three gusset (corner) brackets, as shown.
*Note: if you intend to attach the side panels, leave off the corner bracket on the same side as the 3D printed piece. If you’re not using the side panels, keep the bracket here for additional support!

Step 9. Attach side panel screws.
As before, if you plan to attach HDPE side panels later on, attach the screws for them now, as shown.
Step 10. Attach the expiratory solenoid assembly to the frame.
- First, assemble and attach two gusset (corner) brackets to their hex screws/nuts, then affix to a long (17 ⅞”) leg of the framing, leaving 1” from the end of the piece on each side (that is, leaving space for a vertical piece of 80/20).
- Then, attach three hex screws/nuts to the lower rows of each 90-degree angle bracket as shown; then attach the angle brackets by inserting a short (1mm long) button head screw through the topmost hole of each angle bracket in the opposite direction. These shorter hex screws will screw directly into the solenoid.
- Finally, slide the hex nuts attached to the angle brackets into the T-slot of the 80/20 piece, such that the gusset brackets and solenoid are oriented above the 80/20 piece, as shown. Loosely tighten these in place; you will adjust the position of the solenoid later.


Step 11. Attach gusset (corner) brackets to the opposing 80/20 leg.
Assemble the gusset (corner) brackets with hex screw/nuts as before, and attach them to a long (17 ⅞”) 80/20 piece. Leave 1” of space from each of the side gussets (sufficient space for a vertical 80/20 piece), and affix the third bracket just off-center (to support a centered, vertical 80/20 piece).

Step 12. Assemble the bottom frame components.
Slide the hex nuts on the shorter 80/20 pieces you have assembled into the longer 80/20 slots, and use an Allen key to tighten the screws in place, as shown. The shorter 80/20 legs should be flush with the ends of the longer 80/20 legs when you are done, and the gusset (corner) brackets will help stabilize the frame.
Step 13. Attaching the ventilator “feet” and bottom panel.
If you are attaching the lower, perforated HPDE sheet, insert the rubber grommet. Pre-assemble the shorter (1mm) button head screws to hex nuts, and the leveling mounts (feet) to hex nuts. Use these to attach the lower HPDE panel as shown, by sliding the hex nuts along the long channels on the bottom of the frame assembly; then tighten in place.


Step 14. Attach the respiratory tube segment.
Awesome- almost done with the lower level of the ventilator! As a last step, attach the short segment of respiratory circuit between the “Expiratory outlet bracket to PEEP” and the nearest “22mm to .75NPTM adapter”. You’ll be able to twist this on by hand.

### 2.2 Assembling the frame sides

Step 1. Attach the proportional valve to its mount.
Use the two socket head screws (6mm long) to attach the proportional valve to the 3D printed “proportional valve bracket”. The inlet should be to the right in the orientation shown below.
Step 2. Attach the pressure relief valve to its adapters.
Assemble the T-line push-to-connect adapter, to a female-female ¼” NPT connector, and finally to the Nylon pressure release valve.


Step 3. Attach the luer lock connectors to the luer lock filter mount. These pieces will screw in, with the luer lock portions facing outwards.
Step 4. Assemble the sensor atrium.
Attach the ¼” NPT push-to-connect adapter, check valve, and oxygen sensor into the appropriate holes in the “Sensor Atrium Manifold”, as shown. Do not push the check valve into the device too far, as it may restrict air flow within the atrium.

Step 5. Attach sensor atrium to a short 80/20, and then to the device.
Affix button head screws/nuts to the sensor atrium, with hex nuts facing towards one another, as shown. Slide the hex nuts along T-slots on either side of a short (5 ⅞”) 80/20 piece; then insert this vertically into the device as shown. Tighten into place via the hex screws on the lower gusset (corner) brackets.
*Note: If you are attaching the side panels, be sure to use a SHORT nut on the sensor atrium (the nut on the side with two, farther from the oxygen sensor), and keep the short side facing down when inserting. This will allow the sensor atrium to drop lower and align with the holes in the front panel.


Step 6. Attach the second vertical leg, along the “Expiratory DAR filter bracket”.
As before, slide a short (5 ⅞”) 80/20 piece into the position shown, then tighten the hex screws.
Step 7. Attach the luer lock filter bracket to the newly inserted 80/20 leg.
*Note: If you’re attaching the side panels, use another SHORT 80/20 nut in the uppermost spot on the bracket. We’ll want this part to be as high as possible to match up with the holes on the front panel.

Step 8. Attach the third vertical 80/20 leg, then attach the proportional valve mount. Insert a third, short (5 ⅞”) 80/20 piece, then tighten the hex screw to hold it in place. Use another standard hex screw/nut to attach the proportional valve mount to this piece, towards the inside of the device, such that the push-to-connects roughly align vertically with the push-to-connect on the sensor atrium.
Step 9. Attach the final two vertical 80/20 pieces in the remaining corners.
*Note: If you’re attaching the side panels, now is the time to insert 80/20 nuts on the vertical 80/20 pieces as well as the long 80/20 pieces on the lower frame.


Step 10. Attach the D-Lite.
Attach a blue silicone connector to the “Expiratory DAR filter bracket), on the side within the device. Then, insert the D-Lite between the silicone connector and the nearest “22mm to .75 NPTM adapter”, adjusting the position of the expiratory solenoid assembly until the D-lite is firmly connected at each end. The smaller end of the D-lite should fit within the “22mm to .75 NPTM adapter”. Then, use an Allen key to tighten the hex screws on the 90 degree angle brackets to maintain the position of the solenoid.

Step 11. Attach the pressure release valve and pneumatic tubing.
Cut the pneumatic tubing into three segments: two of length 2.5” (6.35cm), and one of length 5.5” (13.97cm). Insert the long piece between the push-to-connect adapters attached to the pressure regulator and proportional valve. Insert the two shorter tubes into either push-to-connect on the pressure relief valve assembly; then attach these between the sensor atrium and proportional valve push-to-connects, as shown. These tubing lengths should keep the proportional valve fairly centered.


### 2.2 Assembling the frame top

Step 1. Attach the lifting handles.
Use the lifting handle screws (SHCS_0.25-20x0.75_Gr8_ASTM_F1136), with standard hex nuts, to mount the lifting handles to two short (5 ⅞”) pieces of 80/20, such that the handles are centered on the pieces.
Step 2. Prepare all the remaining gusset (corner) brackets.
Attach the hex screws/nuts loosely to the 13 remaining gusset (corner) brackets, so that they can be attached readily in future steps.

Step 3. Attach gusset (corner) brackets, as shown.


Step 4. Cut and punch DIN rail pieces.
Cut the DIN rail to 7 ⅞” (20.0025cm) lengths, punching or drilling holes ½” (1.27cm) from each edge large enough to support the standard button head hex screws.
Step 5. Attach the DIN rails and assemble the rest of the top level.
- Slide two long (17 ⅞”) 80/20 pieces onto one of the shorter pieces, and screw in place. Add an additional gusset (corner) bracket to each long leg, as shown, leaving 1” of space from the end (to support a vertical piece).
- Use a short (1mm) button head hex screw, a zinc washer (W_0.25_FLAT_THICK_GR8_YELLOW_ZINC), and a standard hex nut to attach each end of the DIN rails to the frame, as shown. Slide an additional gusset (corner) bracket between the rails on one side- this will support the central vertical channel on the device.
- Once the DIN rails are roughly in place (exact positions can be adjusted later), use the remaining gusset (corner) brackets and assembled short 80/20 piece, and mirror the other side of the assembly, as shown.


Step 6. Finally, slide the top frame directly into the vertical 80/20 channels of the device, and tighten all hex screws.

Congrats! The basic hardware assembly is complete!

### Part 3. Electronics Assembly

### 3.1 Assembling the Sensor Board

[Image of all components laid out in order/piles, with labels]

You will also need:
- A soldering iron
- Solder
- Helping hands for holding parts while soldering
- Wire cutters (for clipping off long capacitor/resistor legs)
Step 1. Solder the 40-pin stackable RPi header to the Actuator PCB.
Push the pins up from the bottom of the board, as shown, and then solder into place.

Step 2. Solder the 4-pin, 3-pin, and 2-pin 0.1” headers onto the board (positions J2, J3, J4).
Break the pins off the larger header array in units of 4, 2, and 3 using pliers. Insert the short end of the pins into the holes from the top of the board, and solder from below. This will leave the long ends of the pins sticking up vertically from the board, as shown:


Step 3. Solder the 330 Ohm resistor onto the board (position R1).
Bend the resistor legs before inserting into the board from above. Ideally, solder the resistor in place such that the resistor is hovering just above the board. Then, snip the long legs off from the back of the board (cutting above the tiny “cone” formed by the solder) using wire cutters.

Step 4. Solder the two 10 µF, 25V capacitors onto the board (positions C1, C2).
Insert the capacitors from the top of the board until the legs snap into place. Be sure that the longer capacitor leg is inserted into the hole corresponding to the “+” sign. After soldering, snip the long legs off from the back of the board using wire cutters.
Step 5. Solder the TL7660 (the rail splitter for the INA126) onto the board (position U1). Be sure to orient the small circle on the top of the part to the indicated notch drawn on the board.


Step 6. Solder the INA126 (the instrumentation amplifier for the oxygen sensor) onto the board (position U2).
As before, make sure that the notch on the part aligns with the notch drawn on the PCB.
Step 7. Solder the Amphenol 5 INCH-D2-P4V-MINI (differential pressure sensor) onto the board (position U3).
Bend all four pins evenly and orient the part such that the black ports face towards the outside of the board. The pressure lines will attach here.

Step 8. Solder the Adafruit ADS1115 (12-bit ADC) to the board.
First, solder the pins to the ADC itself, with the long ends facing down. Then insert the pins through the board and solder from the back side.

Step 9. Finally, solder the Amphenol 1 PSI-D-4V-MINI (airway pressure sensor) to the board.
As before, bend all four pins together, then insert and solder from the back side of the board. Be sure the ports are facing out: we will attach pressure lines here as well.


### 3.2 Assembling the Actuator Board

[Image of all components laid out in order/piles, with labels]

You will also need:
- A soldering iron
- Solder
- Helping hands for holding parts while soldering
- Wire cutters (for clipping off long capacitor legs)
Step 1. Solder the 40-pin stackable RPi header to the Actuator PCB.
Push the pins up from the bottom of the board, as shown, and then solder into place.

Step 2. Solder the 2-pin 0.1” header onto the board (position J5).
Insert the short end of the pins into the holes from the top of the board, and solder from below. This will leave the long ends of the pins sticking up vertically from the board, as shown:


Step 3. Solder the 100 µF, 16V capacitor onto the board (position C1).
Insert the legs of the capacitor into the slots from the top of the board. The longer leg should be inserted into the side marked “+”. Once the capacitor is soldered in place, use wire cutters to clip off the long legs from the back.

Step 4. Solder the ULN2003A (Darlington array) into place (position U1). Be sure to match the notched end of the part to the notch indicated on the board.
Step 5. Solder the two 6.8 µF, 50V capacitors onto the board (positions C2, C3).
As before, ensure that the longer capacitor legs are inserted through the side marked with the “+”. Once the parts are soldered in, snip the long legs from the back of the board.


Step 6. Solder the 24-to-5 V DC-DC converter (CUI PDQ15-Q24-S5-D) onto the board, as shown.
Step 7. Solder the 3 2-pin screw terminals (5.08mm pitch) to the board, as shown.
Be sure to orient all three such that wires can be screwed into the terminals from the outside of the board (as shown).

Step 8. Finally, jumper the 2-pin header.
You can use a pin jumper (“shunt”) if you have one, or crush the pins together with a pair of pliers, and then solder the two pins together. We display the latter method, below:

Step 9. The actuator board is ready to go!

### 3.3 Assembling the PCB-RPi stack


Step 1. Attach three gas sampling lines to the port on the two pressure sensors.
The differential pressure sensor has two ports. If you have an airway-safe glue, feel free to glue these in place (not required).
Step 2. Begin stacking the board by attaching the DIN rail mounts.
You can pre-”tap” the 3D printed DIN rail mounts using the small screws that come with the Raspberry Pi. Then, screw four of the 16mm standoffs through the Raspberry Pi from above, and into the DIN rail mounts, as shown.

Step 3. Next, add the sensor board.
Connect the sensor board via the stackable headers, then use another four 16mm standoffs to attach the board by screwing these into the original four standoffs, using pliers as needed.
Step 4. Add the actuator board.
Connect the actuator board via the stackable headers, then use the four screws that came with your Raspberry Pi to attach the board, as shown.


### Part 4. Putting it all together

4.1 Wrapping it up.

(Optional step: Attach the side panels using the shorter 80/20 hex screws, as you go.)

Step 1. Attach the DAR filters.
Insert these by hand to the appropriate ports on the front of the device, as shown: these will attach to the sensor atrium and the expiratory DAR filter bracket. The DAR filters indicate which end should face the patient.

Step 2. Attach the luer lock filter.
This can be twisted on by hand to the luer lock adapter at the front of the device.
Step 3. Attach the PEEP valve.
If you’re using a commercial PEEP valve, begin by attaching the blue silicone connector. Then, insert the PEEP valve into the 3D printed “22mm to commercial PEEP adapter”- then plug this assembly into the silicone connector.

Step 4. Attach the power supply.
Pull the tab on the Meanwell power supply to attach it to the DIN rail closest to the back of the device. It may be necessary to adjust the position of this DIN rail to ensure that the power supply is not touching the expiratory solenoid or inlet manifold/pressure regulator. Feel free to reposition as needed!
*Note: if you wish to attach a rear HPDE panel, we recommend inserting the power cable to the power supply through the grommet of the rear panel before insertion of the power supply into the device. Do this now! You can also attach the “Rear Panel Vent”s to the rear panel; they will snap right in.


Step 5. Attach the luer lock plug to the D-Lite.
The third port on the D-Lite (physically removed from the other two) is not needed; plug that now with a luer lock plug.

Step 6. Attach the power and ground wires to the PCB stack. Then wire the proportional valve and solenoid.
Use a small flathead screwdriver to attach the power and ground from the power supply to the PCB stack where indicated. Then do the same for the proportional valve wires and the expiratory solenoid wires: the board indicates which pair goes where!
Step 7. Attach the gas sampling lines to the D-Lite.
Use the luer lock connector on the smaller of the two ports, then connect the two gas sampling lines from the differential pressure sensor (from the same sensor on the Sensor Board).


Step 8. Attach the gas sampling line to the luer lock filter mount adapter.
The third gas sampling line runs from the second pressure sensor; attach this to the inner luer lock adapter on the luer lock filter mount.
Step 9. Plug in any required cables to connect the monitor and keyboard.
Run the cables outside of the box through the rubber grommets; wire ties can assist with cable management.

Congratulations! You’re done!

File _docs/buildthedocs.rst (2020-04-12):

Building the Docs
==================

A very brief summary...

* Docs are configured to be built from ``_docs`` into ``docs``.
* The main page is ``index.rst`` which links to the existing modules
* To add a new page, you can create a new ``.rst`` file if you are writing with Restructuredtext_ , or a `.md` file if you are writing with markdown.

Local Build
-----------

* ``pip install -r requirements.txt``
* ``cd _docs``
* ``make html``

Documentation will be generated into ``docs``

.. _Restructuredtext: https://docutils.sourceforge.io/docs/user/rst/quickref.html

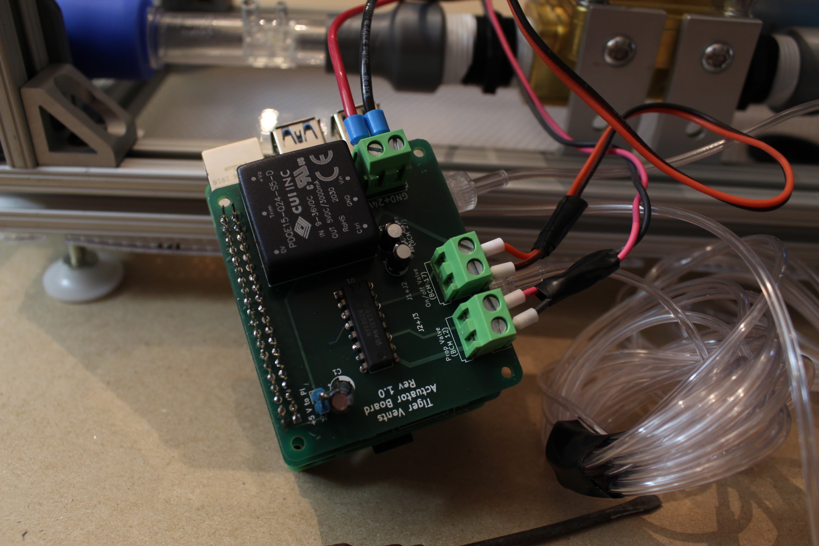
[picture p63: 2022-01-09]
_docs/assets/images/assembly/image46.jpg

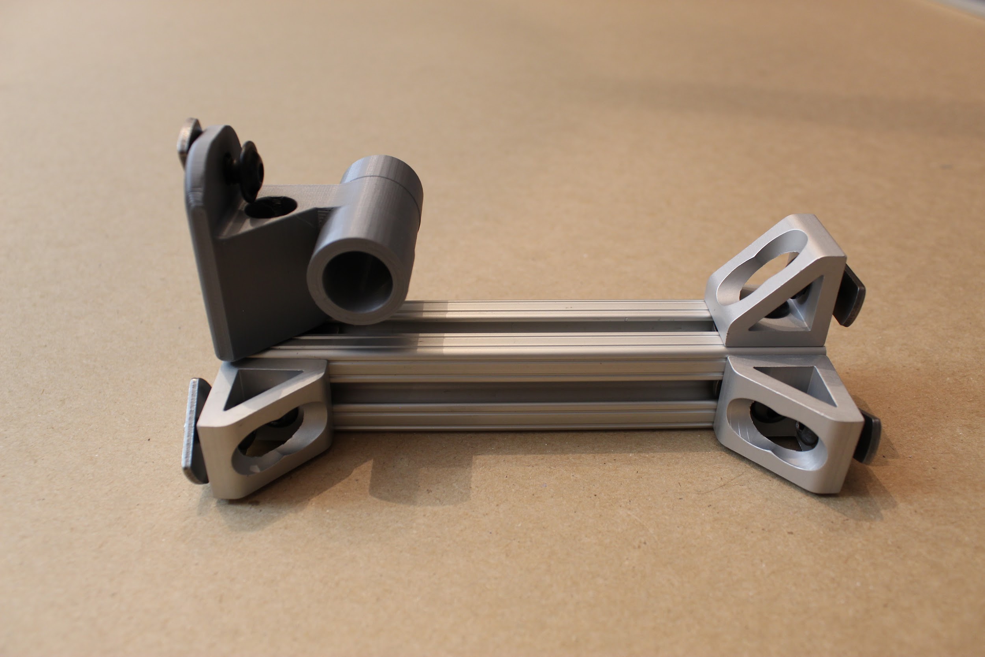
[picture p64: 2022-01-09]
_docs/assets/images/assembly/image50.jpg

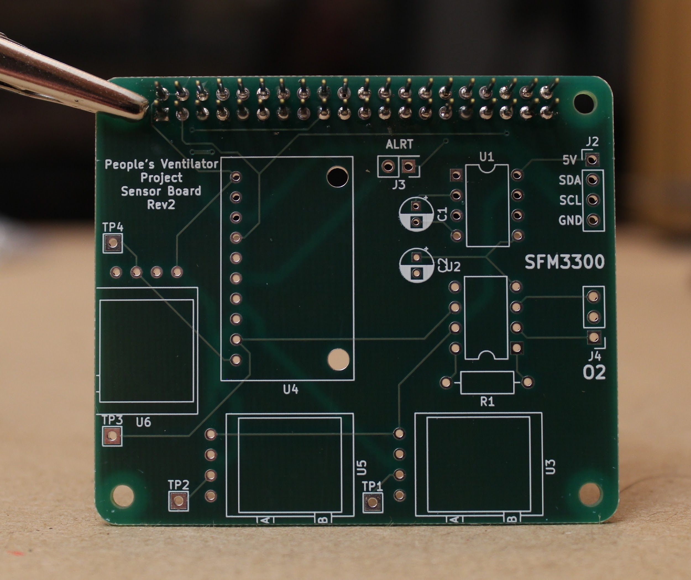
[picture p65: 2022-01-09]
_docs/assets/images/assembly/image73.jpg

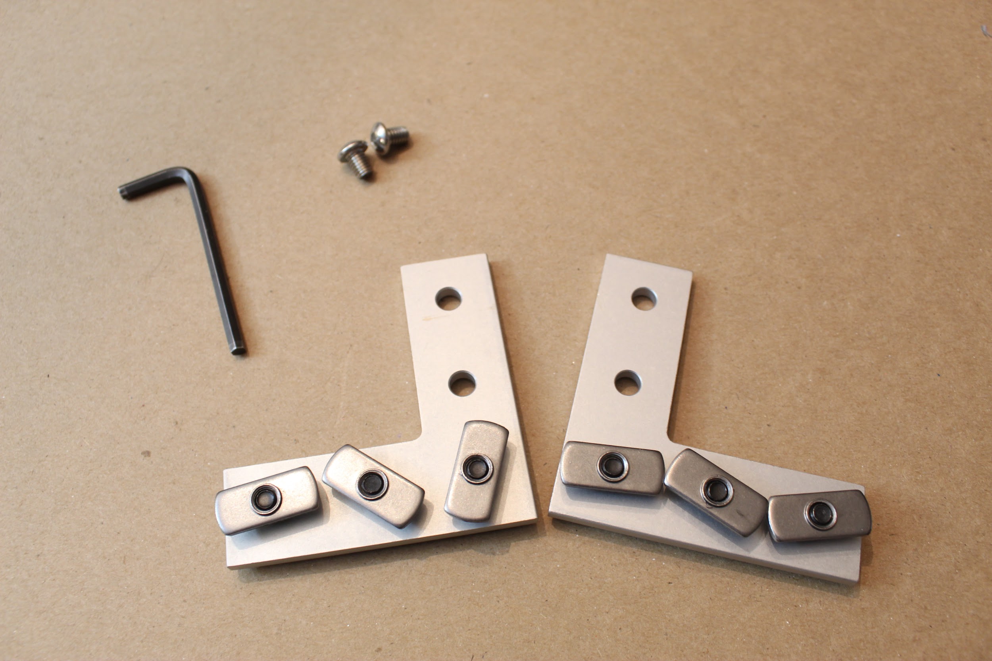
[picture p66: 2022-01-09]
_docs/assets/images/assembly/image23.jpg

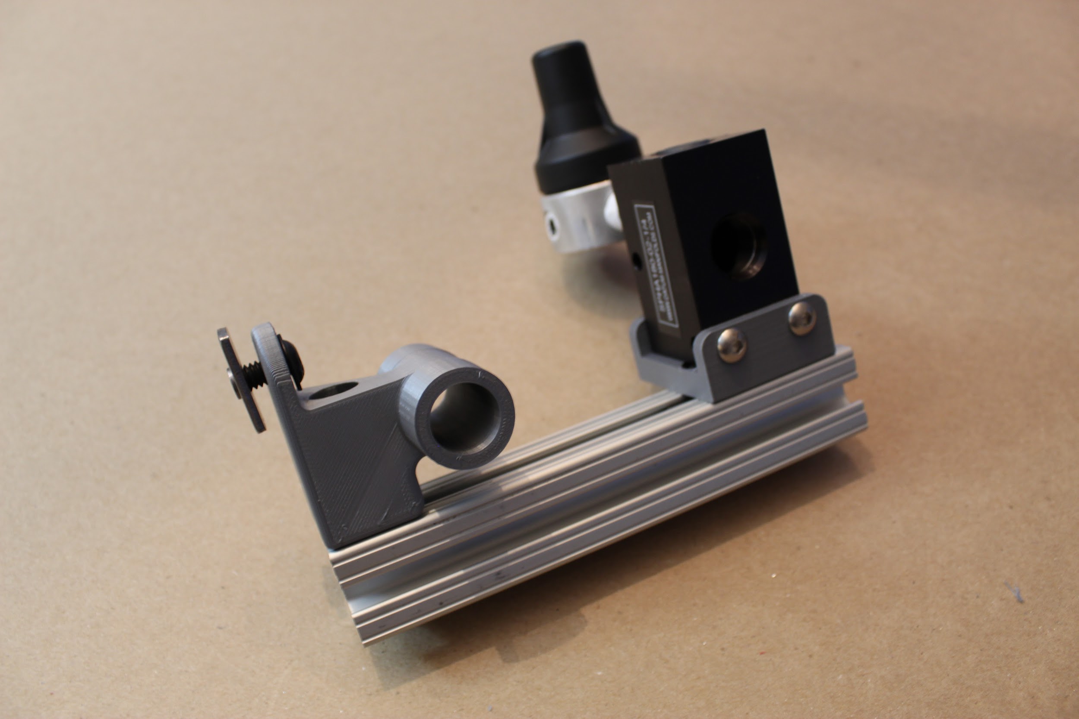
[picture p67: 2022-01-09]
_docs/assets/images/assembly/image89.jpg

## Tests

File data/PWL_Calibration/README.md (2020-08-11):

This folder contains the Python scripts and data from generation of the PWL dataset, and associated sigmoid curve fitting. 

This calibration enabled us to fit a function to the valve "openness" as a function of flow measured through a Sensirion flow sensor vs. proportional valve duty cycle. 

The calibration was then used to determine a more linear and monotonically increasing relationship between a valve setpoint supplied by the controller and the valve "openness".

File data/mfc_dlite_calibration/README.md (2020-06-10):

This data was collected by Philippe Bourrianne (Princeton MAE) and processed by Sophie Dvali (Princeton Physics). 

A mass-flow controller (MFC) was set to output varying rates of flow to a D-Lite spirometer (with a differential pressure sensor attached). 
Voltage data was collected from the differential pressure sensor as the flow varied. Pressure readings from the D-Lite were logged as well.

TV_1 (10 steps from 10 to 100 L/min - 2 successive ramps down and up - physics classical protocol for calibration) (atmospheric pressure at the output of the Flow Block)

TV_2 (10 steps from 10 to 100 L/min - 2 successive ramps down and up - physics classical protocol for calibration) (atmospheric pressure at the output of the Flow Block)

TV_finecalib_1 (many steps from 1 to 100 L/min - for a more detailled calibration - useful to investigate the functional form of a fit) (atmospheric pressure at the output of the Flow Block)

TV_Peep3D_1 (10 steps from 10 to 100 L/min - 2 successive ramps down and up - physics classical protocol for calibration) (3D printed PEEP valve at the output of the Flow Block)

TV_Peepcm10_1 (10 steps from 10 to 100 L/min - 2 successive ramps down and up - physics classical protocol for calibration) (10cmH20 PEEP valve at the output of the Flow Block)

For each test, you have 3 csv files:

i) one ending by ‘_Q.csv’: synchronized data
the first column is time (in s), the second is the order on flow-rate (in L/min) and the third column is the actual flow-rate provided by the mass flow controller (in L/min).

ii) one ending by ‘_DP.csv’: synchronized data
the first column is the time (in s) and the second is the differential pressure DeltaP (from dlite_voltage.csv), and the third is the absolute pressure (from pressure_log.csv).

iii) one ending by ‘_Ave.csv’: averaged data
first column: mean(Q) (in L/min) per step of constant flow-rate
second column: standard deviation of Q (in L/min) per step
third column: mean(DeltaP) (in Pa) per step
fourth column: standard deviation(DeltaP) (in Pa) per step

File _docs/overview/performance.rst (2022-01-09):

Performance
=================



    Representative pressure control breath cycle waveforms for airway pressure and flow out. Test settings: compliance C=20 mL/cm H2O, airway resistance R=20 cm H2O/L/s, PIP=30 cm H2O, PEEP=5 cm H2O.

The completed system was tested with a standard test lung (QuickLung, IngMar Medical, Pittsburgh, PA)
that allowed testing combinations of three lung compliance settings (C=5, 20, and 50 mL cm H2O) and
three airway resistance settings (R=5, 20, and 50 cm H2O/L/s). The figure above shows pressure control 
performance for midpoint settings: C=20 mL/cm H2O, R=20 cm H2O/L/s, PIP=30 cm H2O, PEEP=5 cm H2O. 
PIP is reached within a 300 ms ramp period, then holds for the PIP plateau with minimal fluctuation 
of airway pressure for the remainder of the inspiratory cycle (blue). One the expiratory valve opens, 
exhalation begins and expiratory flow is measured (orange) as the airway pressure drops to PEEP and remains
there for the rest of the PEEP period.
 
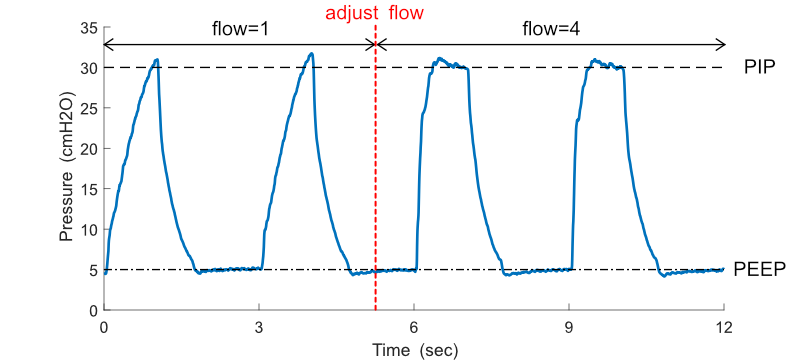
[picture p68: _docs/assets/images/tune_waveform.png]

	
    Demonstration of waveform tuning via flow adjustment.
    If desired, the operator can increase the flow setting through the system GUI to decrease the pressure ramp time.
    Test settings: compliance C=20 mL/cm H2O, airway resistance R=20 cm H2O/L/s, PIP=30 cm H2O, PEEP=5 cm H2O.
 
Some manual adjustment of the pressure waveforms may be warranted depending on the patient, and such adjustment is permitted through a user flow adjustment setting. This flow adjustment setting allows the user to increase the maximum flow rate during the ramp cycle to inflate lungs with higher compliance. The flow setting can be readily changed from the GUI and the control system immediately adapts to the user's input. An example of this flow adjustment is shown in the figure above for four breath cycles. While all cycles reach PIP, the latter two have a higher mean airway pressure, which may be more desirable under certain conditions than the lower mean airway pressure of the former two.

ISO Standards Testing
-----------------------

In order to characterize the PVP's control over a wide range of conditions, we followed FDA Emergency Use Authorization guidelines,
which specify ISO 80601-2-80-2018 for a battery of pressure controlled ventilator standard tests.
We tested the conditions that do not stipulate a leak, and present the results here.
For each configuration the following parameters are listed: the test number (from the table below),
the compliance (C, mL/cm H2O), linear resistance (R, cm H2O/L/s), respiratory frequency (f, breaths/min), peak inspiratory pressure (PIP, cm H2O), positive end-expiratory pressure (PEEP, cm H2O), and flow adjustment setting.

.. csv-table:: Standard test battery from Table 201.105 in ISO 80601-2-80-2018 for pressure controlled ventilators
   :file: /assets/csv/eua_test.csv
   :widths: 3,5,5,5,5,5,5,5,5
   :header-rows: 1

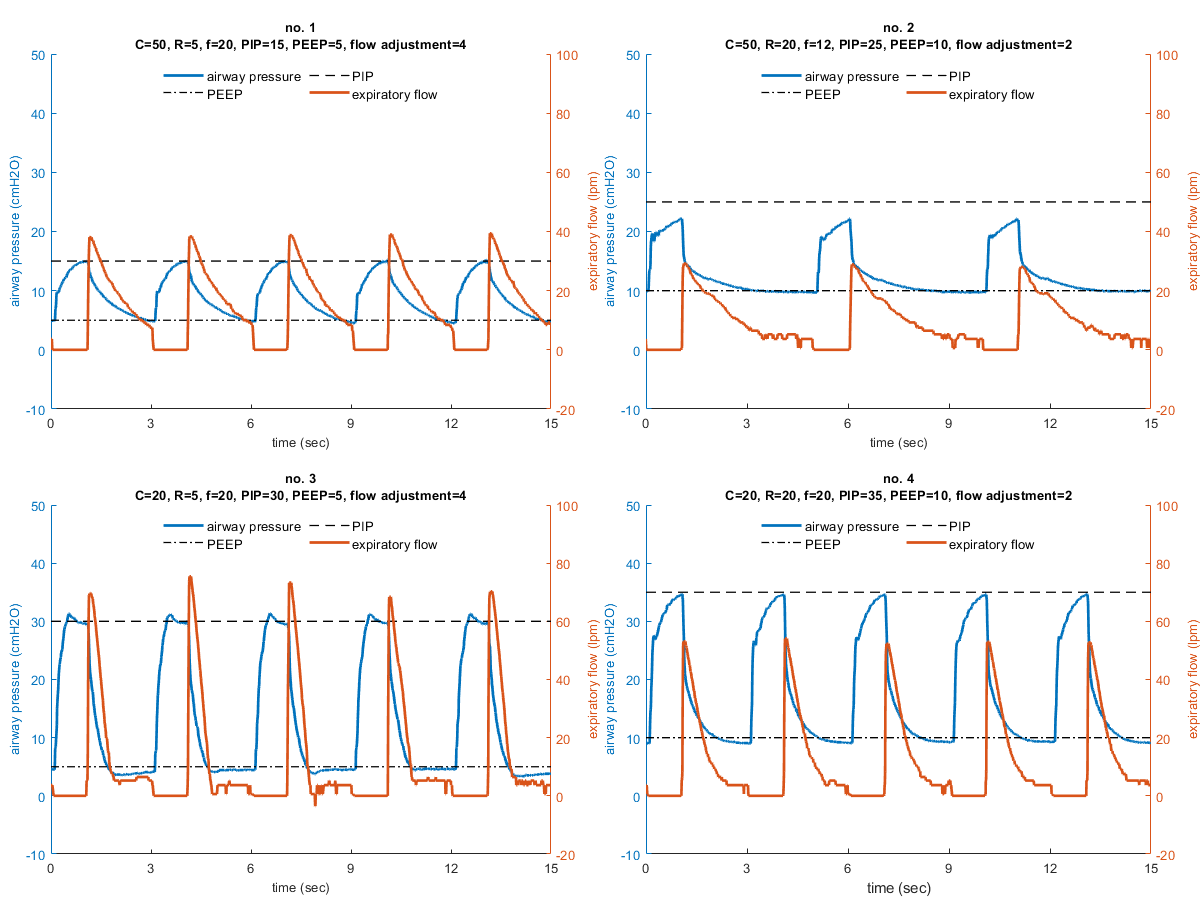
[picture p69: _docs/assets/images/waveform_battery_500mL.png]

	
    Performance results of the ISO 80601-2-80-2018 pressure controlled ventilator standard tests with an intended delivered tidal volume of 500 mL. For each configuration the following parameters are listed: the test number (from table 201.105 in the ISO standard), the compliance (C, mL/cm H2O), linear resistance (R, cm H2O/L/s), respiratory frequency (f, breaths/min), peak inspiratory pressure (PIP, cm H2O), positive end-expiratory pressure (PEEP, cm H2O), and flow adjustment setting. PIP is reached in every test condition except for case 2, which is approximately 2.4 cm H2O below the set point.

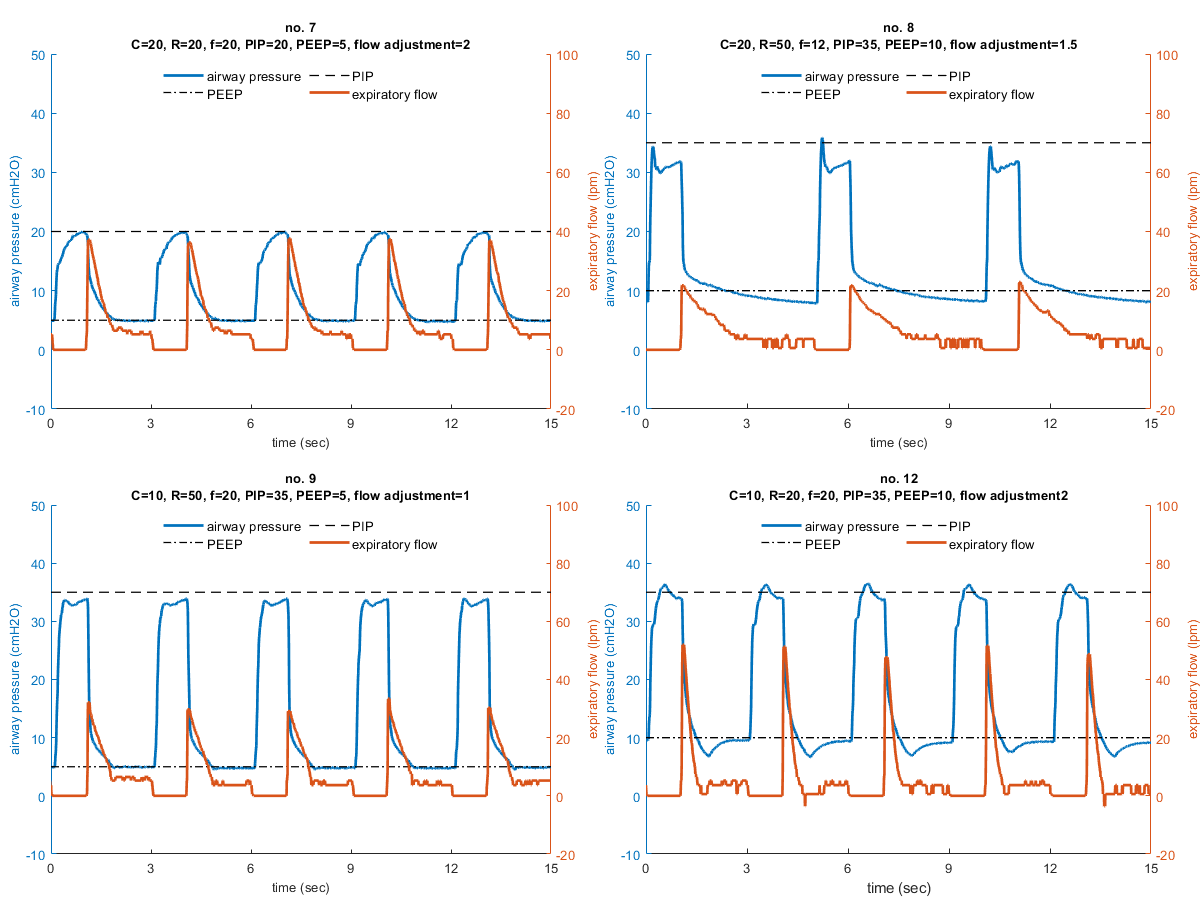
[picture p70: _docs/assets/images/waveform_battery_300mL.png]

	
    Performance results of the ISO 80601-2-80-2018 pressure controlled ventilator standard tests with an intended delivered tidal volume of 300 mL. For each configuration the following parameters are listed: the test number (from table 201.105 in the ISO standard), the compliance (C, mL/cm H2O), linear resistance (R, cm H2O/L/s), respiratory frequency (breaths/min), peak inspiratory pressure (PIP, cm H2O), positive end-expiratory pressure (PEEP, cm H2O), and flow adjustment setting. PIP is reached in every test condition.

These tests cover an array of conditions,
and more difficult test cases involve a high airway pressure coupled with a low lung compliance (case nos. 8 and 9).
Under these conditions, if the inspiratory flow rate during the ramp phase is too high, 
the high airway resistance will produce a transient spike in airway pressure which can greatly overshoot the PIP value.
For this reason, the system uses a low initial flow setting and allows the clinican to increase the flow rate if necessary.

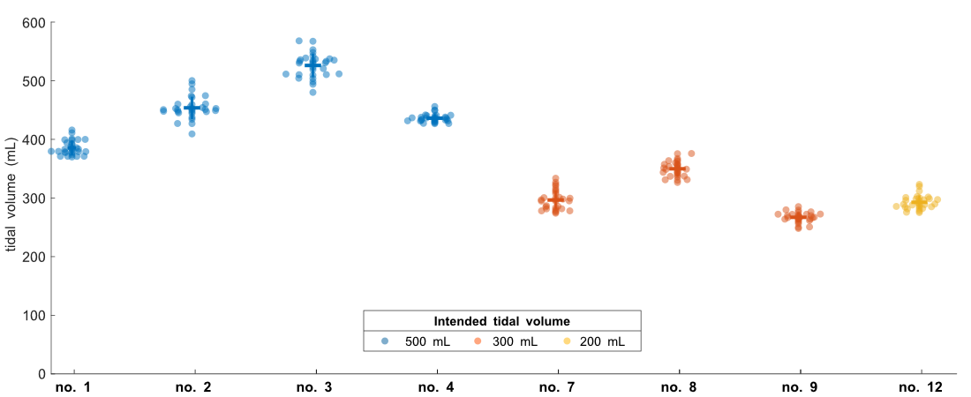
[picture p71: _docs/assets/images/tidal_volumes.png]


    Tidal volume performance for the ISO 80601-2-80-2018 pressure controlled ventilator standard tests, averaged across 30 breath cycles for each condition.

The PVP integrates expiratory flow to monitor the tidal volume, which is not directly set in pressure controlled ventilation, but is an important parameter. Of the test conditions in the ISO standard, four that we tested intended a nominal delivered tidal volume of 500 mL, three intended 300 mL, and one intended 200 mL. For most cases, the estimated tidal volume has a tight spread clustered within 20% of the intended value.

Breath Detection
------------------

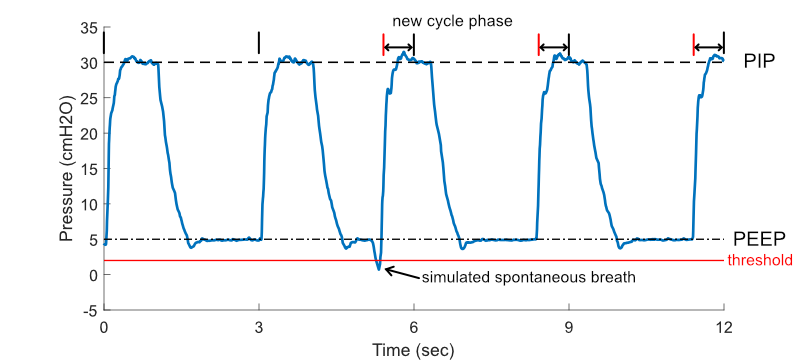
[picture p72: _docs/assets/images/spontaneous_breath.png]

	
    Spontaneous breath detection.
	
A patient-initiated breath after exhalation will result in a momentary drop in PEEP. PVP may optionally detect these transient decreases to trigger a new pressure-controlled breath cycle. We tested this functionality by triggering numerous breaths out of phase with the intended inspiratory cycle, using a QuickTrigger (IngMar Medical, Pittsburgh, PA) to momentarily open the test lung during PEEP and simulate this transient drop of pressure.

High Pressure Detection
--------------------------

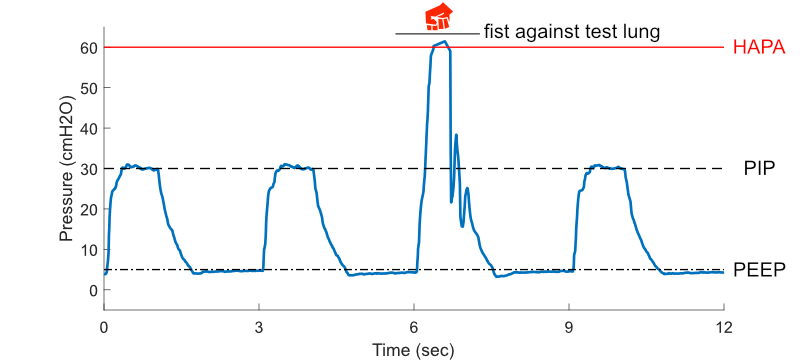
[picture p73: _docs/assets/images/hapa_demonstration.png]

	
    High pressure alarm demonstration.
	
Above is a demonstration of the PVP's high airway pressure alarm (HAPA). An airway blockage results in a high airway pressure (above 60 cm H2O) that the system corrects within ~500 ms.
Test settings: compliance C=20 mL/cm H2O, airway resistance R=20 cm H2O/L/s, PIP=30 cm H2O, PEEP=5 cm H2O.

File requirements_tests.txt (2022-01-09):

pytest~=5.4.1
pytest-qt==3.3.0
pytest-timeout
coveralls
pytest-cov
pylint
coveralls

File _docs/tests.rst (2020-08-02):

tests package
=============

Submodules
----------

tests.pigpio\_mocks module
--------------------------

.. automodule:: tests.pigpio_mocks
    :members:
    :undoc-members:
    :show-inheritance:

tests.test\_alarms module
-------------------------

.. automodule:: tests.test_alarms
    :members:
    :undoc-members:
    :show-inheritance:

tests.test\_controller module
-----------------------------

.. automodule:: tests.test_controller
    :members:
    :undoc-members:
    :show-inheritance:

tests.test\_coordinator module
------------------------------

.. automodule:: tests.test_coordinator
    :members:
    :undoc-members:
    :show-inheritance:

tests.test\_gui module
----------------------

.. automodule:: tests.test_gui
    :members:
    :undoc-members:
    :show-inheritance:

tests.test\_io\_devices module
------------------------------

.. automodule:: tests.test_io_devices
    :members:
    :undoc-members:
    :show-inheritance:

tests.test\_io\_hal module
--------------------------

.. automodule:: tests.test_io_hal
    :members:
    :undoc-members:
    :show-inheritance:

tests.test\_io\_pins module
---------------------------

.. automodule:: tests.test_io_pins
    :members:
    :undoc-members:
    :show-inheritance:

tests.test\_io\_sensors module
------------------------------

.. automodule:: tests.test_io_sensors
    :members:
    :undoc-members:
    :show-inheritance:

tests.test\_io\_valves module
-----------------------------

.. automodule:: tests.test_io_valves
    :members:
    :undoc-members:
    :show-inheritance:

tests.test\_logging module
--------------------------

.. automodule:: tests.test_logging
    :members:
    :undoc-members:
    :show-inheritance:

Module contents
---------------

.. automodule:: tests
    :members:
    :undoc-members:
    :show-inheritance:

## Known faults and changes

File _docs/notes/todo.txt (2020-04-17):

* fade color for older traces
* buttons to control length of history

- design specific API for 

- be ablee to both receive and emit alarms

- save ui state and load

- threads
	main ui thread
	communication thread
		qthread checkig on socket
		timeout on wait, signal process management that haven't received message
	process management thread
		periodic callbck

- logging
	check on available space
	delete/rotate logs

- command line option to not reload state

to do:
	diagram of the UI, ownership, calling relationship
	ui/communication thred - two queues, ingoing and outcoing
	ui/process management thread - tell process manager when new values
	logging
	testing - document test cases, conditions, signals and slots
	cli parameters
	error handling
	add requirements to requirements doc

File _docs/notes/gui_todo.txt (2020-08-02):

* when gui starts check if controller already running - be able to be restarted by controller
* make technical alarm class and display that can also display the error message & etc.
* alarm objects shouldnt' have a deactivation method.
* remove temp and humitdity
* check that logging space limit is set overall rather than per-logger
* docker image so that ventilator starts on system startup
* ui mode for testinga

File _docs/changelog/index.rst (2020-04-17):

.. _changelog:

Changelog
==========

Version 0.0
-----------
.. toctree::
    :maxdepth: 2

    v0.0.2
    v0.0.1
    v0.0.0

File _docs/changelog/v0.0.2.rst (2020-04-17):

.. _changelog_v002:

v0.0.2 (April xxth, 2020)
-------------------------

* Refactored gui into a module, splitting ``widgets``, ``styles``, and ``defaults``.

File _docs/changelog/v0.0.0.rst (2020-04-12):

.. _changelog_v000:

v0.0.0 (April 12th, 2020)
-------------------------

Example of a changelog entry!!!

* We fixed this
* and this
* and this

.. warning::

    but we didn't do this thing

.. todo::

    and we still have to do this other thing.

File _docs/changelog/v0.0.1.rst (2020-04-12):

.. _changelog_v001:

v0.0.1 (April 12th, 2020)
-------------------------

* Added changelog
* Moved requirements for building docs to `requirements_docs.txt` so regular program reqs are a bit lighter.
* added autosummaries
* added additional resources & documentation files, with examples for adding external files like pdfs

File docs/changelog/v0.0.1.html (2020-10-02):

- »
- Changelog »
- v0.0.1 (April 12th, 2020)
- View page source

# v0.0.1 (April 12th, 2020)¶

- Added changelog
- Moved requirements for building docs to requirements_docs.txt so regular program reqs are a bit lighter.
- added autosummaries
- added additional resources & documentation files, with examples for adding external files like pdfs

Next Previous

© Copyright 2020, jonny saunders et al

Built with Sphinx (http://sphinx-doc.org/) using a theme (https://github.com/rtfd/sphinx_rtd_theme) provided by Read the Docs (https://readthedocs.org).

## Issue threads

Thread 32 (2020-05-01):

CohenLabPrinceton/pvp #32: Timeouts on get_ and set_ functions with decorators?

mschottdorf, 2020-05-01:
How do we set timeouts universally? Should we use decorators? Could use something along these lines:
```
import signal
import time
from contextlib import contextmanager

class TimeoutException(Exception): pass

@contextmanager
def time_limit(seconds):
    def signal_handler(signum, frame):
        raise TimeoutException("Timed out!")
    signal.signal(signal.SIGALRM, signal_handler)
    signal.alarm(seconds)
    try:
        yield
    finally:
        signal.alarm(0)

def timelimitdecorator(func):
    def wrapper(*args, **kwargs):
        try:
            with time_limit(10):
                func(*args, **kwargs)
        except TimeoutException as e:
            print("Timed out!")
    return wrapper
```

Then on a function
```
@timelimitdecorator
def foo(sleeptime):
    time.sleep(sleeptime)
    print("hello")
```

We get a timeout on foo(11), but not on foo(1).

sunnyszy, 2020-05-01:
I would propose that let's think about what functions need a timeout. I feel GUI <-> coordinator, coordinator <-> controller don't really need it as they are within the same process, and the function is basically returned a copy of the value.

Coordinator IPC definitely needs a timeout. And does controller <-> sensor need a timeout?

mschottdorf, 2020-05-03:
I guess, we'll have to see how the sensor-abstraction layer turns out

sunnyszy, 2020-05-04:
Yes, I agree. I would suggest let's hold this issue a bit until we have more information about the requirement and the assumption about the sensor layers. To give a more concrete example, if the sensor call blocking probability is ~1 failure/month, it might not worth implementing this complexity into the logic. Remind that the coordinator will restart the controller process if it hangs.

sneakers-the-rat, 2020-05-04:
somehow didn't see this, v clever. think this is a great idea (although i would name the decorator `timeout` :) )

PR #46 (2020-05-08): Draft implementation of @properties for locks & exceptions
This is a rough draft - mostly untested and I didn't go through the project to apply @locked. exception logger doesn't actually log anything, just raises whatever it's passed.

Nevertheless, I figured I'd open up a feature branch & draft PR to collect thoughts & code. 

closes #32 
closes #35 
closes #38
closed 2020-05-08 by mschottdorf

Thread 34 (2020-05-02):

CohenLabPrinceton/pvp #34: IndexError: empty axes in `control_module.__analyze_last_waveform`

sneakers-the-rat, 2020-05-02:
Have had this happen a few times if i leave the program running for a few minutes in the background. branch is current w/ https://github.com/CohenLabPrinceton/Ventilator-Dev/commit/32d64d05f622e445633393847e63ef8afbfd11f9

I think we should have the tests run for longer, ive seen a few errors come up only after the program has been running for a few minutes. or is there some way to make control module simulation generate values as fast as possible and not simulate a sampling rate?

```
Traceback (most recent call last):
  File "/usr/local/Cellar/python/3.7.7/Frameworks/Python.framework/Versions/3.7/lib/python3.7/threading.py", line 926, in _bootstrap_inner
    self.run()
  File "/usr/local/Cellar/python/3.7.7/Frameworks/Python.framework/Versions/3.7/lib/python3.7/threading.py", line 870, in run
    self._target(*self._args, **self._kwargs)
  File "/Users/jonny/git/Ventilator-Dev/vent/controller/control_module.py", line 714, in _start_mainloop
    self._PID_update(dt = dt)                               # Update the PID Controller
  File "/Users/jonny/git/Ventilator-Dev/vent/controller/control_module.py", line 500, in _PID_update
    self.__analyze_last_waveform()    # Analyze last waveform
  File "/Users/jonny/git/Ventilator-Dev/vent/controller/control_module.py", line 251, in __analyze_last_waveform
    self._DATA_PEEP = np.percentile(pressure[ pressure < np.mean(pressure)], 20 )
  File "<__array_function__ internals>", line 6, in percentile
  File "/usr/local/lib/python3.7/site-packages/numpy/lib/function_base.py", line 3713, in percentile
    a, q, axis, out, overwrite_input, interpolation, keepdims)
  File "/usr/local/lib/python3.7/site-packages/numpy/lib/function_base.py", line 3833, in _quantile_unchecked
    interpolation=interpolation)
  File "/usr/local/lib/python3.7/site-packages/numpy/lib/function_base.py", line 3410, in _ureduce
    r = func(a, **kwargs)
  File "/usr/local/lib/python3.7/site-packages/numpy/lib/function_base.py", line 3948, in _quantile_ureduce_func
    x1 = take(ap, indices_below, axis=axis) * weights_below
  File "<__array_function__ internals>", line 6, in take
  File "/usr/local/lib/python3.7/site-packages/numpy/core/fromnumeric.py", line 194, in take
    return _wrapfunc(a, 'take', indices, axis=axis, out=out, mode=mode)
  File "/usr/local/lib/python3.7/site-packages/numpy/core/fromnumeric.py", line 61, in _wrapfunc
    return bound(*args, **kwds)
IndexError: cannot do a non-empty take from an empty axes.```

mschottdorf, 2020-05-02:
Thanks for finding! I'll try to reproduce it!

mschottdorf, 2020-05-02:
I'm not sure what caused it, but I had a few dead stubs left over when I transitioned from the ring-buffer to deque. I've removed all this in the new PR. Might have resolved this bug as well.

I ran the test 20x, and let the code run for ~330.000 cycles. This all worked well.

[image]

sneakers-the-rat, 2020-05-03:
sorry for not providing reproducible error, thanks for checking it out. i'll let ya know if anything else pops up but by and large the simulation has worked well :)

sneakers-the-rat, 2020-05-05:
same thing happened again w/ but only after like 15m https://github.com/CohenLabPrinceton/Ventilator-Dev/commit/17504a8914445993811f5abcf2b9fbd4a2d92769 

going to run again w/ pdb for this and the complex number error and get back 2 u

sneakers-the-rat, 2020-05-05:
the gui stays alive, but the controller dies. seems like controller should be able to swallow numerical errors -- exception handling in the main loop

mschottdorf, 2020-05-05:
Yeah, can be done (just return a np.nan for peep and pip), but I really want to know want is going on here... might be something important

sneakers-the-rat, 2020-05-05:
traced it back to the `Qin` value from `SimulatedPropValve`

sneakers-the-rat, 2020-05-05:
actually wait no `x` in the line before is nan first

mschottdorf, 2020-05-05:
I'm pretty sure that can only happen if the pressure is np.nan - sounds like a bug in the balloon simulation. Can you give me parameters to try to reproduce this here?

sneakers-the-rat, 2020-05-05:
yes i believe the balloon is having some beef with natural law:

```python
pprint(self.Balloon.__dict__)
{'P0': 0,
 'PC': 20,
 'current_flow': -0.9999999999999993,
 'current_pressure': nan,
 'current_volume': -2.6030784139434933,
 'delay': False,
 'fio2': 13990.878703428589,
 'humidity': 77.49196868074476,
 'leak': True,
 'max_volume': 6,
 'min_volume': 1.5,
 'r_real': nan,
 'temperature': 362.6075413405974}```

sneakers-the-rat, 2020-05-05:
`np.clip` volume to min zero?

sneakers-the-rat, 2020-05-05:
clamped volume to min 0 and i'm getting some cool other stuff like temperature shooting off to a billion. i think it might be that the simulation expects `dt` to be very small and having a large `dt` causes big error. i get the bug most when I minimize and remaximize the GUI window so it could be that the simulation hangs while that long draw is happening. all the more important to get into separate processes asap

sneakers-the-rat, 2020-05-05:
dk if that's just a simulator problem or if that's in the control logic, if it's just simulator i don't know that we need to spend a ton of time making it bulletproof. I do think that having erratic `dt`s would be a good test though.

mschottdorf, 2020-05-05:
I'll spend some time today on the simulator. This should be fixed... I think you're right, and this is likely a problem in the calculation of the OU process with large dt. There are a few other things in the simulator, that need fixing as well. E.g. controlled by solenoids, flows should be proportional to pressure differences. I'll add this right now

sneakers-the-rat, 2020-05-05:
ok cool. 10m runtime and the problem hasn't returned

sneakers-the-rat, 2020-05-05:
but ya in `Balloon.update` I just went like

```python
    def update(self, dt):  # Performs an update of duration dt [seconds]
        self.current_volume += self.current_flow * dt
        self.current_volume  = np.max([0, self.current_volume])
```

mschottdorf, 2020-05-05:
[image]
look at that leaky balloon... that cannot be right!

mschottdorf, 2020-05-05:
Alright, I've made a PR with improved balloon physics. Hopefully, clipping the volume at zero is not necessary anymore - it shouldn't happen

sneakers-the-rat, 2020-05-05:
idk much about balloons but that balloon has got some attitude

mschottdorf, 2020-05-07:
PR is merged

closed 2020-05-07 by mschottdorf

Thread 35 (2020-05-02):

CohenLabPrinceton/pvp #35: Locks handled as @properties and a careful programming proposition

sneakers-the-rat, 2020-05-02:
**Note: this is something I think we should save effort on until we get a working prototype out, but want to write it down**

Reading through the code in a bit more detail while setting up alarms, and some of this locking is making me nervous. Please understand my intentions as genuine and goode and not trying to code shame. I raised this during our last call and just wanted to follow up

**Problem:**
locks, well, lock. and so if a lock is ever acquired without being released, and there are no timeouts, then the program hangs. The following code makes me nervous:

https://github.com/CohenLabPrinceton/Ventilator-Dev/blob/32d64d05f622e445633393847e63ef8afbfd11f9/vent/coordinator/coordinator.py#L142
```python
while not self.stopping.is_set():
    sensor_values = self.control_module.get_sensors()
    self.lock.acquire()
    self.COPY_sensor_values = sensor_values
    self.last_message_timestamp = sensor_values.timestamp
    self.lock.release()
    for name in [ValueName.PIP,
                 ValueName.PIP_TIME,
                 ValueName.PEEP,
                 ValueName.BREATHS_PER_MINUTE,
                 ValueName.INSPIRATION_TIME_SEC]:
        self.lock.acquire()
        in_control_settings = name not in self.COPY_control_settings
        self.lock.release()
        if in_control_settings:
            control_setting = self.control_module.get_control(name)
            self.lock.acquire()
            self.COPY_control_settings[name] = control_setting
            self.lock.release()

        self.lock.acquire()
        disagreed_tentative = name in self.COPY_tentative_control_settings and self.COPY_tentative_control_settings[name] != self.COPY_control_settings[
                    name]
        self.lock.release()
        if disagreed_tentative:
            self.lock.acquire()
            tentative_control_setting = self.COPY_tentative_control_settings[name]
            self.lock.release()
            self.control_module.set_control(tentative_control_setting)
            self.lock.acquire()
            self.COPY_control_settings[name] = self.control_module.get_control(name)
            self.lock.release()
    # sleep 10 ms
    time.sleep(0.01)
```

Given the number of times the lock is accessed, and the degree of nesting, this seems like a pretty difficult to maintain/error-prone method of thread management. 

**Proposal:**
From what I understand, the lock is just acquired and released whenever any of these set of attributes are accessed. 

let's use properties, this is what they were born to do.

Observe the following extraordinarily careful pattern that I believe we should follow as a general pattern for repetitively called methods

```python
import traceback
import functools

# some global stack param
MAX_STACK_DEPTH = 20

def locked(func):
    """
    Wrapper to use as decorator, handle lock logic for a
    @property

    Arguments:
        func (callable): function to wrap
    """

    # define a function to return that wraps the inner
    # function around some standardized error handling
    # logic

    # use .wraps to preserve inner method identity
    @functools.wraps(func)
    def lock_wrapper(self, *args, **kwargs):
        ret = None

        try:
            self.lock.acquire()
            ret = func(self, *args, **kwargs)
        except Exception as e:
            log_exception(
                e, 
                traceback.extract_tb(MAX_STACK_DEPTH)
            )
        finally:
            self.lock.release()

        return ret

    return lock_wrapper

class CoordinatorBase:
    def __init__(self, sim_mode=False):

        self.lock = threading.Lock()

        self.control_module = get_control_module(sim_mode)
        self._sensor_values = None

    @locked
    @property
    def sensor_values(self):
        return self._sensor_values

    @locked
    @sensor_values.setter
    def sensor_values(self, sensor_values):
        self._sensor_values = sensor_values
```

This would allow every lock acquisition and release to be replaced with standard attribute set/get methods. ie instead of
`
# set
self.lock.acquire()
self.COPY_sensor_values = ...
self.lock.release()

# get
def get_sensors(self) -> SensorValues:
    self.lock.acquire()
    sensor_values = self.COPY_sensor_values
    self.lock.release()
    # return res
    return sensor_values
`
(which is also retrieved by an additonal method `get_sensors` that acquires/releases the lock) 

you just use
`
# set
self.sensor_values = ...

# get
self.sensor_values
`

The benefits are of course not just aesthetic, but guarantee that the lock is always released due to the use of `finally` and that any exceptions are always logged.

sneakers-the-rat, 2020-05-02:
sorry laptop battery dying and wanted to post to save before i could finish commenting code!!!

mschottdorf, 2020-05-03:
makes perfect sense to me, had suggested something similar for timeouts. Let's talk about this in our next meeting, but I'd love to adapt this soon. Will make the code much cleaner!

PR #46 (2020-05-08): Draft implementation of @properties for locks & exceptions
This is a rough draft - mostly untested and I didn't go through the project to apply @locked. exception logger doesn't actually log anything, just raises whatever it's passed.

Nevertheless, I figured I'd open up a feature branch & draft PR to collect thoughts & code. 

closes #32 
closes #35 
closes #38
closed 2020-05-08 by mschottdorf

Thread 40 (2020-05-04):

CohenLabPrinceton/pvp #40: Complex numbers

sneakers-the-rat, 2020-05-04:
The simulator sometimes breaks and starts spitting out complex values for pressure:

```
Exception in thread Thread-3:
Traceback (most recent call last):
  File "/usr/local/Cellar/python/3.7.7/Frameworks/Python.framework/Versions/3.7/lib/python3.7/threading.py", line 926, in _bootstrap_inner
    self.run()
  File "/usr/local/Cellar/python/3.7.7/Frameworks/Python.framework/Versions/3.7/lib/python3.7/threading.py", line 870, in run
    self._target(*self._args, **self._kwargs)
  File "/Users/jonny/git/Ventilator-Dev/vent/controller/control_module.py", line 716, in _start_mainloop
    self._PID_update(dt = dt)                               # Update the PID Controller
  File "/Users/jonny/git/Ventilator-Dev/vent/controller/control_module.py", line 469, in _PID_update
    if self._DATA_PRESSURE < 1.1*self.__SET_PEEP:
TypeError: '<' not supported between instances of 'complex' and 'float'
```

tracing it back the complex value gets assigned here:
https://github.com/CohenLabPrinceton/Ventilator-Dev/blob/87a83f5964ffbc1f40c558b07716e6f3977ca44c/vent/controller/control_module.py#L620

but i have no idea why it would be float sometimes and not other times....

mschottdorf, 2020-05-04:
intriguing.. Could be related to negative volumes, i.e. small errors if more air flows out than in. Will investigate. Thanks!

mschottdorf, 2020-05-05:
This might have been related to the other issue with tormented physics

mschottdorf, 2020-05-07:
PR is merged, fingers crossed!

closed 2020-05-07 by mschottdorf

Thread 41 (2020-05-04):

CohenLabPrinceton/pvp #41: Implementing Alarms

sneakers-the-rat, 2020-05-04:
Making a single place to talk about implementing alarms (as it applies to code, the slack channel is more for organizing w/ rest of team). I'll be editing this post as I work so it may change

My current understanding of what we had planned
* Controller and GUI both check for alarms, GUI serves as a double-check on alarm checking from controller (did we both get an alarm just now?) and otherwise takes its alarms from controller. 
* Alarms will be 'sticky' and be displayed until user dismisses them
* User will have option to mute alarms for specific time - i'm thinking all alarms, and alarms for a particular value.
* ... more but can't remember good

Questions
* logging? who logs the alarms. I think it sorta makes sense to have the GUI log them since the GUI will be the one displaying, generating text for them, and dismissing them, but also see value in dual-logging (`logging` module makes it easy to have multiple logs for different objects)
* sound? I can make some alarm sounds (in a former life i was a sound engineer for ~7 years & apprenticed with a sound designer) but figure if we can use alarm sounds that would be familiar it would be better

sneakers-the-rat, 2020-05-05:
Currently the user sets the desired value of PIP as a control, but the value returned by `get_sensors` is pressure, which is also the value that users set limits on in the gui. Do we
* map the safe_range of pressure onto PIP, PEEP, etc? (eg. max range of pressure is max allowed pip?
or
* have `get_sensors` return measured PIP, PEEP, etc. and give each of them a `monitor` object to set ranges?

mschottdorf, 2020-05-05:
For the protocol, the controller is logging past alarms (and past waveforms) up to 100 entries. It would be good to also save this sporadically in a file, possibly by the coordinator

sneakers-the-rat, 2020-05-08:
I was looking for how to send down limits on monitored values like `FiO2` and as far as I can tell there isn't such a thing in the controller. It looks like a lot of the variables that manage alarms in the controller are hardcoded. This makes it so it can't trigger an alarm for, eg. FiO2 going out of range. It also means that the controller needs to have its code modified every time there is a new value to check -- eg. if we want to trigger an alarm off of `IE_RATIO` . The gui has all of its alarm ranges generated programmatically from `values.py`, so this is not the case. I see two options, a) have the controller and gui both generate alarms and have the coordinator house an `alarm_manager` that can handle the logic of combining them, b) the controller can be rewritten such that it programmatically updates variables from `values.py` s.t. it can generate alarms for all of the alarmed values.

these are the places i found with hardcoded variables:

https://github.com/CohenLabPrinceton/Ventilator-Dev/blob/c7fddba3528d2c049805b97804308019f28d255f/vent/controller/control_module.py#L100
https://github.com/CohenLabPrinceton/Ventilator-Dev/blob/c7fddba3528d2c049805b97804308019f28d255f/vent/controller/control_module.py#L146
https://github.com/CohenLabPrinceton/Ventilator-Dev/blob/c7fddba3528d2c049805b97804308019f28d255f/vent/controller/control_module.py#L303

this would be pretty trivial to implement. it looks like you need, for each, value, min, max, and lastset. in your `__init__` it could look like

```python
self.controls = {}
for val_name, val_params in values.CONTROL.items():
    self.controls[val_name] = {
        'value': None,
        'min': val_params['safe_range'][0],
        'max': val_params['safe_range'][1],
        'lastset': time.time()
```

you could make the different versions you have for each of the variables, eg `COPY` and the like as well.

so then the rest of your methods could be updated to follow that pattern. like `set_control`:

```python
if control_setting.name in ValueName:
    self.controls[control_setting.name]['value'] = control_setting.value
    self.controls[control_setting.name]['min'] = control_setting.min
```

and likewise the `__update_alarms` method could be something like 

```python
for control_name, control_params in self.controls.items():
    self.__test_critical_levels(min=control_params['min'], max = control_params['max'], value=control_params['value'], name = control_name)
```

mschottdorf, 2020-05-08:
makes perfect sense to me. Yes, the code does not allow to send down alarms (yet)

sneakers-the-rat, 2020-05-12:
I'm thinking that basically all alarm checking logic should come out of the controller except for the high-pressure response. I'll make the gui and controller reciprocal so that the gui also pulls controls from the controller so that if the controller drops PIP the gui will reflect that. 

as i mentioned in the meeting earlier today, there's another way of categorizing values, `continuous` or `phasic` (idk that terminology doesn't seem right) - measurements that are made continuously like pressure and those that are computed once per breath cycle. I'm going to add that as an additional parameterization of a value, and also keep track of the breath cycle number and send that in `SensorValues`. that'll be necessary for defining alarm conditions based on breath cycle values

mschottdorf, 2020-05-12:
The controller is also getting quite complex. Would be great to outsource some of that alarm code

sneakers-the-rat, 2020-05-14:
Currently i have two alarm parameters:

if an alarm `latch` es, it a) does not decrement its severity even when the values fall back into a lower-severity range and b) is only cleared when both 1) the user has requested that the alarm be cleared and 2) the alarm values return to the ‘off’ range.
if an alarm is `persistent`, it a) is decremented in severity when values fall into a lower-severity range, b) can be cleared from the gui at any time, but c) will not be removed from the GUI until the user manually clears it (otherwise alarms are cleared when they return to OFF)
is there a case where we wouldn’t want a `persistent` alarm to not `latch` ? otherwise I will remove the `persistent` attribute

sneakers-the-rat, 2020-05-14:
4:51
Currently it is possible to clear an alarm
indefinitely - silencing an alarm will cause that alarm to not be raised again until it returns to OFF severity.
for a period of time - the gui will provide the user a choice of snooze times, and the alarm will not be raised again until the time is up.
they are mutually exclusive — if a timeout is provided, the alarm will not be re-raised if it goes OFF and back on.
should all alarm dismissals be timed? ie. if an alarm is cleared without an explicit snooze, it will not be raised until it goes OFF and back ON or some default time passes?

sneakers-the-rat, 2020-05-19:
preserving some todo items from the pr

https://github.com/CohenLabPrinceton/Ventilator-Dev/pull/64#discussion_r426008278

https://github.com/CohenLabPrinceton/Ventilator-Dev/pull/64#discussion_r426010901

https://github.com/CohenLabPrinceton/Ventilator-Dev/pull/64#discussion_r426011154

https://github.com/CohenLabPrinceton/Ventilator-Dev/pull/64#discussion_r426012813

https://github.com/CohenLabPrinceton/Ventilator-Dev/pull/64#discussion_r426013542

https://github.com/CohenLabPrinceton/Ventilator-Dev/pull/64#discussion_r426016985

https://github.com/CohenLabPrinceton/Ventilator-Dev/pull/64#discussion_r426018333

https://github.com/CohenLabPrinceton/Ventilator-Dev/pull/64#discussion_r426023529

closed 2020-05-29 by sneakers-the-rat

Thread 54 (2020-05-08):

CohenLabPrinceton/pvp #54: Logging

sneakers-the-rat, 2020-05-08:
Let's keep track of what we need to do for logging!!!

considerations
* make a standardized logging class that each object can instantiate, but don't necessarily make a centralized logging object that needs to be fed information.
* size - don't fill up the disk with logs. rotate logs, check how much space is left etc.

mschottdorf, 2020-05-09:
To merge this with the other issue-> Considering the finite live time of the components, and future maintenance of the device, we have to **keep track of open/close cycles**, and **time since installing a particular sensor/valve**.

sunnyszy, 2020-05-15:
Python has a powerful logging system: https://docs.python.org/3.8/howto/logging-cookbook.html
I wonder whether we can leverage that.

Ideally, anything that can be serialized can be logged. But we may not want to log things that need to be read back again (e.g., persistent config).

sunnyszy, 2020-05-19:
I forgot the schedule for this. Will you implement this @mschottdorf? Or I can take a look and implement this.

mschottdorf, 2020-05-19:
I've you have a free afternoon, go for it! I haven't had the time to do it

mschottdorf, 2020-05-19:
My plan was implementing two things:

- python's logging for general logs across threads, mostly because it is thread safe, and 
- A hdf5-system, similar to [jonny's work](https://github.com/wehr-lab/autopilot/blob/2to3/autopilot/core/subject.py) within the controller to keep track of the waveforms.

sunnyszy, 2020-05-19:
Why not I do part one and you do part two? I used logging before.

mschottdorf, 2020-05-19:
go for it; for part 2, I'd probably write a class, and let the instance live in the controller thread. Any objections?

sunnyszy, 2020-05-19:
I second that. It would be easier to make it stateless, otherwise, you have to persist this class as well.

sneakers-the-rat, 2020-05-29:
Closing b/c logging facility has been written.

closed 2020-05-29 by sneakers-the-rat

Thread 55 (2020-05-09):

CohenLabPrinceton/pvp #55: IndexError: cannot do a non-empty take from an empty axes.

mschottdorf, 2020-05-09:
Might be related to Jonny's reported bugs. When re-scaling, or switching between desktops, or running for a long time, the simulator crashes, or simulated temperatures/pressures go haywire.

I'm trying to figures out what is going on.

```
ms81@pni-18c02xj50tjgh5 Ventilator-Dev % ipython ./vent/main.py
qt.qpa.fonts: Populating font family aliases took 248 ms. Replace uses of missing font family "Fira Code" with one that exists to avoid this cost.
/Users/ms81/Ventilator-Dev/vent/controller/control_module.py:706: RuntimeWarning: invalid value encountered in double_scalars
  self.r_real = (3 * self.current_volume / (4 * np.pi)) ** (1 / 3)
/usr/local/lib/python3.7/site-packages/pyqtgraph/graphicsItems/PlotCurveItem.py:153: RuntimeWarning: All-NaN slice encountered
  b = (np.nanmin(d), np.nanmax(d))
Exception in thread Thread-1:
Traceback (most recent call last):
  File "/usr/local/Cellar/python/3.7.7/Frameworks/Python.framework/Versions/3.7/lib/python3.7/threading.py", line 926, in _bootstrap_inner
    self.run()
  File "/usr/local/Cellar/python/3.7.7/Frameworks/Python.framework/Versions/3.7/lib/python3.7/threading.py", line 870, in run
    self._target(*self._args, **self._kwargs)
  File "/Users/ms81/Ventilator-Dev/vent/controller/control_module.py", line 805, in _start_mainloop
    self._PID_update(dt = dt)                               # Update the PID Controller
  File "/Users/ms81/Ventilator-Dev/vent/controller/control_module.py", line 522, in _PID_update
    self.__analyze_last_waveform()    # Analyze last waveform
  File "/Users/ms81/Ventilator-Dev/vent/controller/control_module.py", line 264, in __analyze_last_waveform
    self._DATA_PEEP = np.percentile(pressure[ pressure < np.mean(pressure)], 20 )
  File "<__array_function__ internals>", line 6, in percentile
  File "/usr/local/lib/python3.7/site-packages/numpy/lib/function_base.py", line 3706, in percentile
    a, q, axis, out, overwrite_input, interpolation, keepdims)
  File "/usr/local/lib/python3.7/site-packages/numpy/lib/function_base.py", line 3826, in _quantile_unchecked
    interpolation=interpolation)
  File "/usr/local/lib/python3.7/site-packages/numpy/lib/function_base.py", line 3403, in _ureduce
    r = func(a, **kwargs)
  File "/usr/local/lib/python3.7/site-packages/numpy/lib/function_base.py", line 3941, in _quantile_ureduce_func
    x1 = take(ap, indices_below, axis=axis) * weights_below
  File "<__array_function__ internals>", line 6, in take
  File "/usr/local/lib/python3.7/site-packages/numpy/core/fromnumeric.py", line 194, in take
    return _wrapfunc(a, 'take', indices, axis=axis, out=out, mode=mode)
  File "/usr/local/lib/python3.7/site-packages/numpy/core/fromnumeric.py", line 61, in _wrapfunc
    return bound(*args, **kwds)
IndexError: cannot do a non-empty take from an empty axes.
```

mschottdorf, 2020-05-10:
This bug is caused extremely long update-times. Here is a snapshot of the update times (in seconds) per controller iteration just before the controller went crazy:
[image]

I don't know how to fix this (yet), but dt is considerably longer than an entire breath cycle.

sunnyszy, 2020-05-11:
When I replicate this bug, I found another bug that the GUI in my environment won't start. See: https://github.com/CohenLabPrinceton/Ventilator-Dev/issues/60

mschottdorf, 2020-05-13:
With the current PR, the controller can now dead with long waits between updates:

[image]

But we have to figure out why this is happening.

sunnyszy, 2020-05-14:
This looks pretty cool!

sneakers-the-rat, 2020-05-14:
it looks like it can't find the font I added to the repo, so I'll have to troubleshoot that. the reason I packaged a font is because to specify q generic font you have to build the entire font db which is costly, like 5 seconds costly.

mschottdorf, 2020-05-17:
On Grant's suggestion: For the plots above, I was running `coordinator = get_coordinator(single_process=True, sim_mode=True)`. I've done the same `coordinator = get_coordinator(single_process=False, sim_mode=True)`. This seems to solve the timeout-issue. 

In its own thread, and with a goal sleep-time of 10ms between cycles in the controller, the average controller-loop-time was ~11.5ms. This plot is the loop-time density over ~30min of recording (while I was working on my laptop, UI in the background :-) ).

[image]

mschottdorf, 2020-05-21:
I'll close this. Problem was apparently solved by threading

closed 2020-05-21 by mschottdorf

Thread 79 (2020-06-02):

CohenLabPrinceton/pvp #79: Pressurized Gas Requirements (ISO 80601-2-80)

CohenLabPrinceton, 2020-06-02:
a) If the VENTILATORY SUPPORT EQUIPMENT is intended to be connected to a MEDICAL GAS PIPELINE SYSTEM complying with ISO 7396‐1, then it

- [ ] a1: Must comply with 80601 throughout RATED input range. 

- [ ] a2: shall not cause an unacceptable RISK under the SINGLE FAULT CONDITION of 1 000 kPa.

b) If VSE has max RATED input pressure in excess of 600 kPA, then the SFC is 1200 kPa.

- [ ] validate that we are below 600 kPa for rated input pressure.

CohenLabPrinceton, 2020-06-02:
Notes from ISO 80601:

_TL;DR = it's OK to have a regulator to keep the flow/pressure where we want. Also, even with overpressure we want flow to continue through the VBS and it's OK if flow rates are outside tolerance at this point._ 

NOTE 1 Internal pressure regulators can be needed to accommodate the SINGLE FAULT CONDITION of maximum input pressure, as well as the RATED range of input pressure.

NOTE 2 Under the SINGLE FAULT CONDITION of overpressure, it is desirable for gas to continue to flow to the VBS. Under this condition, the flowrate from the VENTILATORY SUPPORT EQUIPMENT is likely to be outside of its specification._

CohenLabPrinceton, 2020-06-02:
I've checked off (a1) because I think it just means that the VBS needs to function as described for all pressure within the RATED range we provide in our spec sheet.

zajdel, 2020-06-02:
For (b), our regulator is to be set to deliver 50 psi input pressure, which is 344 kPa < 600 kPa.

zajdel, 2020-06-02:
Concerning (a2), our regulator (SMC AR25-02BG, datasheet attached) has a maximum operating pressure of 1000 kPa and a proof pressure of 1500 kPa.

closed 2020-06-02 by zajdel

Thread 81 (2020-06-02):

CohenLabPrinceton/pvp #81: Pressure/Flow Compatibility Requirements (201.4.11.101.2)

CohenLabPrinceton, 2020-06-02:
If the VENTILATORY SUPPORT EQUIPMENT is intended to be connected to a MEDICAL GAS PIPELINE SYSTEM complying with ISO 7396‐1, then

- [ ] a) the RATED range of input pressure shall cover the range specified in ISO 7396‐1, and

 b) under NORMAL CONDITION,

- [ ] 1) the maximum 10 s average input flowrate required by the VENTILATORY SUPPORT EQUIPMENT for each gas shall not exceed 60 l/min at a pressure of 280 kPa, measured at the gas input port, and

- [ ] 2) the transient input flowrate shall not exceed 200 l/min averaged for 3 s, **OR..**.

- [ ] (OR) 3) the ACCOMPANYING DOCUMENTS shall disclose the following: 

- [ ] i) the maximum 10 s average input flowrate required by the VENTILATORY SUPPORT EQUIPMENT for each gas at a pressure of 280 kPa, measured at the gas input port;

- [ ] ii) the maximum transient input flowrate averaged for 3 s required by the VENTILATORY SUPPORT EQUIPMENT for each gas at a pressure of 280 kPa, measured at the gas input port;

- [ ] iii) a warning to the effect that this ventilator is a high‐flow device and should only be connected to a pipeline installation designed using a diversity factor that allows for the indicated high flowrate at a specified number of terminal outlets, in order to avoid exceeding the pipeline design flowrate, thereby minimizing the risk that the ventilator interferes with the operation of adjacent equipment.

CohenLabPrinceton, 2020-06-02:
I am a bit confused about the language "Average input flowrate *required* by the VSE..." Sounds like we need to show that our 10s average is <= 60 l/min at the gas input port. Seems like we'd address this with actual flow data that we'd compile into a figure.

CohenLabPrinceton, 2020-06-02:
We also need to establish a test protocol to collect these data and decide who will do it.

juliennelachance, 2020-06-16:
Yes, it sounds like we should just record pressure and flow logs over the course of 10+ cycles. The flow rate should be well within range.

CohenLabPrinceton, 2020-06-17:
@juliennelachance we need to fix the pressure at 280 as well. @zajdel can we get these data relatively soon since we don’t need alarms or anything fancy?

sneakers-the-rat, 2020-06-22:
dk if i'm needed on this issue, unassign me if no gui stuff needed <3

closed 2020-10-09 by CohenLabPrinceton

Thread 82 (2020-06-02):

CohenLabPrinceton/pvp #82: Overstretch on the test-lung during remote testing

CohenLabPrinceton, 2020-06-02:
Test-lung over-stretched and damaged the springs and the lung bag itself. 

Context: Manuel was remotely testing control and noted unstable and surprising behaviors in the system; possibly stuck or erratic valves? 

Short-term Responses:

- [ ] Mechanical limiter to stop this happening again

- [ ] Swap to cheap test lung bag until we're confident

- [ ] Rush order springs

Long-term Responses--Manuel/Tom?

CohenLabPrinceton, 2020-06-02:
Tom ordered springs already.

zajdel, 2020-06-02:
We've swapped to the balloon bag already. I have also moved the pressure sensor the right location.

I'm testing the mechanical limiter that Julie spec'd some time ago, since it fits into the manifold we're currently using and testing that.

zajdel, 2020-06-02:
So the pressure relief valve was installed in the wrong direction. It doesn't easily fit into the manifold the way it's supposed to, so I put it in the wrong way. I would say we had a mechanical failure of pressure limiting that could have been avoided. Earlier versions of Manuel's code would terminate while leaving the inspiratory valve open. In this 50 psi system, that leads to instant inflation without a proper pressure cutoff. I'm going to make sure that I know how this new pressure valve needs to be installed.

mschottdorf, 2020-06-02:
I looked at the logs from this morning. The situation happened in conjunction of three failures: (1) inspiratory valve stayed open, while expiratory valve was closed, (2) pressure measurement was not configured properly; therefore HAPA was not triggered [from the logs: recorded pressure always <50cmH2O] and (3) hardware failure of the relief valve.

To avoid this happening in the future:

1. While the code implements high-airway-pressure-alert and management, it was not triggered [Currently set to 80 cmH2O, opens the expiratory valve, and closed the inspiratory valve]. Need to make sure that config files is the right one for the device. Possible tests could be: atmospheric pressure should be around 0. What else?

2. To test for sluggish valves, could `set_ex` and `set_in` multiple times. 

3. Make flowing the relief valve a mandatory test before playing with hardware.

zajdel, 2020-06-02:
The relief valve is for sure working now, so that's a backup safety that we have now, though that's up to 0.75 psi (50 cm H2O), so that should be the hardware-enforced limit.

CohenLabPrinceton, 2020-06-02:
@zajdel @mschottdorf thanks for tracking things down. I'm curious that the pressure never exceeded 50 cmH2O and I want to make sure this is real because I would have thought that enough pressure to overinflate that lung and overcome compliance would have gone higher than 50 cmH2O. Can we please confirm that the pressure sensor works properly; might have just been where it was positioned?

mschottdorf, 2020-06-02:
Let's do this tomorrow @zajdel; I've changed a few minor things in the code, but the pressure remains surprisingly low. Can we produce a defined pressure in the system, and I check what the controller believes the pressure to be?

zajdel, 2020-06-03:
I have a physical gauge I can attach in the system near the pressure sensor. That should help at least verify the pressure. Another way would be to remove the test lung and run at full tilt, letting the pressure relief valve set the system pressure to a known 50 cmH2O.

zajdel, 2020-06-04:
Test lung sent to IngMar Medical for repairs, and Manuel and I spent some time calibrating the pressure sensor in the airway, catching an important scaling error caused by our using a differential pressure sensor. This, along with safeties that Manuel put in the code, makes it so that this will not happen again!

closed 2020-06-04 by zajdel

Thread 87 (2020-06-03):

CohenLabPrinceton/pvp #87: TestReport: Testing Error Reporting

ProfDJCohen, 2020-06-03:
Ref: CR501 201.5.101.3

- [ ] Updated?

VENTILATORY SUPPORT EQUIPMENT testing errors
--

- [ ] a) For the purposes of this document, declared tolerances shall include the measurement uncertainty.

- [ ] b) The MANUFACTURER shall disclose the measurement uncertainty of each disclosed tolerance in the technical description.

ProfDJCohen, 2020-06-03:
@zajdel @CommReteris @sneakers-the-rat @Sophie We need to make sure that we have a table of measurement uncertainty, etc. that we report in our labeling parameters and for every measured/derived parameter.

sneakers-the-rat, 2020-06-03:
should the UI display static +/- % error tolerance message next to measured parameters?

CohenLabPrinceton, 2020-06-03:
Nope. These need to go in the labeling documentation and disclosures in the manual, not the machine UI

CohenLabPrinceton, 2020-06-18:
Update: @zajdel will test this using testing conditions for Pressure Control table from the ISO table. @SophieDvali can help fit the data if needed.

SophieDvali, 2020-06-19:
I'm a little confused about the wording here, does this just mean we have to report the uncertainty of all measured quantities? Is this separate from the EUA items for reporting the error of the individual measured quantities?

CohenLabPrinceton, 2020-06-22:
@SophieDvali these are the same things. We need to report the error for any quantities we show the user. I think if you have the error values for flow and volume then we should be good.

sneakers-the-rat, 2020-06-22:
unassigning myself since this is a docs thing for the hardware team. lmk if you need help using the docs tho.

closed 2020-10-09 by CohenLabPrinceton

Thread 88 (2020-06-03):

CohenLabPrinceton/pvp #88: TestReport: UI and Units of Measure

ProfDJCohen, 2020-06-03:
Ref 1: CR501 201.7.4.3 / 80601-2-80

Units of measure

a) All gas volume, flowrate and leakage specifications:

- [ ] 1) shall be expressed at STPD (STANDARD TEMPERATURE AND PRESSURE, DRY);

- [ ] 2) except those associated with the VBS which shall be expressed at BTPS (BODY

TEMPERATURE AND PRESSURE, SATURATED).

- [ ] bb) The unit of AIRWAY PRESSURE measurement shall be capable of being configured to be expressed in hPa

ProfDJCohen, 2020-06-03:
@sneakers-the-rat we need a 'units' setting where we can switch to hPa. I am not sure about the reporting of BTPS since we're not measuring anything that would be affected by that (I think).

sneakers-the-rat, 2020-06-20:
changing value over 2 orders of magnitude is actually sorta tricky when ur space constrained. got most of the way there but need to quit for the night.

sneakers-the-rat, 2020-06-21:
https://github.com/CohenLabPrinceton/Ventilator-Dev/commit/4c7c929df47941c2f3d7aad93c31c2311e44b339

sneakers-the-rat, 2020-06-21:
surprisingly hard to do

closed 2020-06-21 by sneakers-the-rat

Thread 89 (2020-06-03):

CohenLabPrinceton/pvp #89: TestReport: Certification and Spec'ing of Single Use Parts

ProfDJCohen, 2020-06-03:
- [ ] a) if the VENTILATORY SUPPORT EQUIPMENT, its parts or ACCESSORIES are intended for single use,

information on characteristics and technical factors known to the MANUFACTURER that could pose a
RISK if the VENTILATORY SUPPORT EQUIPMENT, its parts or ACCESSORIES were reused.

b) if the VENTILATORY SUPPORT EQUIPMENT, its parts or ACCESSORIES are intended for single use,
information regarding:

- [ ] 1) the intended duration of use; and

- [ ] 2) the consequences for the PATIENT if use is beyond the specified duration of use.

ProfDJCohen, 2020-06-03:
@julie @zajdel all of our disposable parts for single-use need spec-sheets and justifications for duration of use/issues if not complied with. This is really important for the documentation I think. We'll need a complete list of all EXTERNAL accessories, biocompatibility of these, and certification info.

zajdel, 2020-06-16:
List of single-use parts:
- PEEP valve
- HMEF
- DAR filters
- Respiratory tubing

CohenLabPrinceton, 2020-06-18:
@SophieDvali maybe can help get the spec sheets for these. 

Where does this go in the test report? Manual?

closed 2020-10-09 by CohenLabPrinceton

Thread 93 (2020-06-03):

CohenLabPrinceton/pvp #93: TestReport: Oxygen combustion safety

ProfDJCohen, 2020-06-03:
Ref: CR501 Clause 11 / IEC 60601-1 (11.2.2.1 is MISSING)

**RISK of fire in an OXYGEN RICH ENVIRONMENT**

If the medical device is intended to be used with oxygen:

- [ ] 	Describe means of protection to reduce the risk of ignition

If the medical device is intended to be used with oxygen operating at medical gas pipeline pressures:

- [ ] Describe means of protection to taken to ensure that auto-ignition from adiabatic compression cannot occur

ProfDJCohen, 2020-06-03:
AAMI CR502 implies that auto-ignition is only a risk at 5 bar or higher. 50 psig is 3.5 bar, so I think we're OK there. However, we need careful discussion of combustion risk mitigation.

juliennelachance, 2020-06-03:
Ignition risk mitigation includes: no contactors (like relays: everything we're using is solid-state) so as to avoid arcs; enclosure of the electronics; avoiding aluminum in the oxygen pathway; etc.

CohenLabPrinceton, 2020-06-03:
@juliennelachance thanks, but we need to be exhaustive, so please do not say ‘etc’. If there is something else that helps, write it explicitly. A concise, bulleted list is best.

CohenLabPrinceton, 2020-06-18:
@zajdel speaker could be an issue.

closed 2020-10-09 by CohenLabPrinceton

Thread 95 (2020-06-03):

CohenLabPrinceton/pvp #95: TestReport: Cleaning and Disinfection

ProfDJCohen, 2020-06-03:
CLEANING and DISINFECTION of ME EQUIPMENT or ME SYSTEM

Describe the cleaning/disinfection protocol of the medical device and accessories

See ISO 80601-2-80 snapshot below (couldn't copy-paste)
[image]

ProfDJCohen, 2020-06-03:
We need to discuss how to clean the inside of the vent and any 3D printed parts. We can discuss in our risk management assessment that we use dual HEPA filters specifically to ensure that anything leaving the vent is sterile so nothing can reach the patient that isn't sterile UNLESS there is a problem in the respiratory circuit itself, which is single-use. Thoughts?

CohenLabPrinceton, 2020-06-18:
Need @DrDan opinion on this. Likely household ammonia-based cleaning following a standard protocol.
What about the 3D printed manifolds? How do we clean PLA/ABS/PETG. 
@SophieDvali can you look into the solenoid valves and the 3D printed manifolds? DrDan should be able to help recommend cleaning solutions.

SophieDvali, 2020-06-22:
There's a bunch of Czech labs that tested all sorts of cleaning methods for 3D printed face shields (some of the tests were done specifically on COVID-19) they include things like UV-C, Isopropanol and Hydrogen peroxide (the full list is here: https://help.prusa3d.com/en/article/prusa-face-shield-disinfection_125457/ ) This is for PETG specifically. Since this is for face shields some of these might not work for our case.

closed 2020-10-09 by CohenLabPrinceton

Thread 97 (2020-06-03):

CohenLabPrinceton/pvp #97: TestReport: Alternate power supply

CohenLabPrinceton, 2020-06-03:
Additional requirements Interruption of the power supply/SUPPLY MAINS   to ME EQUIPMENT

Describe:

- [ ] •Means used to provide alternate power source

- [ ] •Means to determine the state of the alternate power source

- [ ] •Run time of alternate power source 

- [ ] •Alarm indications

CohenLabPrinceton, 2020-06-03:
@sneakers-the-rat we may need to incorporate an alarm for this in the UI that detects IF the alternate supply is in use. @zajdel easiest way to do this for an arbitrary UPS power supply? Alternately, we can spec one that actually alarms us when it is in use using an audible alarm.

sneakers-the-rat, 2020-06-03:
I have a battery pack, but would be useful to have the battery pack that we plan on using for the final thing so i can test code that checks on power source

CohenLabPrinceton, 2020-06-03:
@sneakers-the-rat I think we need an actual UPS that can keep the whole machine running for this. It might be an optional standard so we could just say 'not included', but it's better to have it. The Pi battery is also important, and maybe that would only engage when the UPS is needed. @juliennelachance do you and Rengo have a favorite battery pack we were going to use? Otherwise I'd say just use a UPS because battery packs are fire risks.

zajdel, 2020-06-03:
Is the UPS to be included within the project enclosure, or can it be external?

CohenLabPrinceton, 2020-06-04:
External ok for EUA @zajdel

zajdel, 2020-06-05:
The UPS we use in the lab (and many others, it seems) comes with a USB communication port. I am not knowledgeable on this subject, but this USB port is designed to be used with UPS monitoring software. I will look into what we would need to do to poll the UPS and get a status update.

Here's a tutorial about doing just that with a Pi.
[](https://medium.com/@mike.reider/monitor-cyberpower-ups-devices-with-raspberry-pi-99559725dbb8)

Looks like the NUT (Network UPS Tools) library, or something like it, will need to be installed.

sneakers-the-rat, 2020-06-05:
lmk whatever ups you have/how to query it and i can add status/timer in ui

CohenLabPrinceton, 2020-06-07:
If the UPS has simple LEDs that light to indicate charge/function, that's also fine. COnsidering that a UPS is optional for the EUA, I'd say spend minimal time here. @sneakers-the-rat @zajdel

zajdel, 2020-06-09:
Our UPS doesn't have an LED, but its LCD shows if it's running off of the battery or not.

We will use an [OMNI1500LCDT](https://www.tripplite.com/omnismart-lcd-120v-1500va-810w-line-interactive-ups-tower-lcd-display-usb-port-energy-star~OMNI1500LCDT) which is rated 810W output which should cover our system.

To determine runtime on battery, I would get a power monitor (like a Kill a Watt) and monitor the vent while it runs at 20 breaths/minute to estimate power consumption.  Then we'd compare that against the capacity of the battery, which is cited as 7.5 minutes at half load (405 Watts). Our power use is likely <50 W, so I would estimate on the order of an hour of battery power. Still, better measure the power output to be certain.

closed 2020-10-09 by CohenLabPrinceton

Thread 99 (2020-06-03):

CohenLabPrinceton/pvp #99: TestReport: Pressure Controlled Vent standard

CohenLabPrinceton, 2020-06-03:
This is a big one. I've uploaded direct from the ISO standard for this. This needs a real discussion. Someone besides me should go through and parse each instruction here as a checkbox. 

[ISO 80601-2-80-2018_PCBreath.pdf](https://github.com/CohenLabPrinceton/Ventilator-Dev/files/4726153/ISO.80601-2-80-2018_PCBreath.pdf)

CohenLabPrinceton, 2020-06-03:
@mschottdorf @juliennelachance @zajdel we need to have a meeting go through this I think and design the test approach and make sure it's rock-solid so we don't have to repeat it and ensure we log data, etc.

zajdel, 2020-06-03:
I see why we have the QuickLung. That takes care of issues 7-10 in the test set up.

[image]

Checklist for required test components:
- [ ]  1. Ventilatory support equipment under test (that would be the Dinky)
- [ ]  2. Pressure sensor (proximal) - we need to finalize the connector/port we are using.
- [ ]  3. Flow sensor - sensiron probably works - the rise time requirement only applies for volume-controlled breath types
- [ ]  4. Artificial leakage - Not sure what this requires yet.
- [ ] 5. Data acquisition system - minimum sample rate of 200 samples/s (do we achieve this?)
- [ ] 6. Temperature sensor - We have one but I have not yet set it up. Should communicate via SPI with the main board. We have connectors for this.
- [ ] 7. Series resistance with test lung (QuickLung adjustable)
- [ ] 8. Pressure sensor with a 10% to 90% rise time of no greater than 10 ms (double-check this for our 1psi 4v mini - Quicklung port)
- [ ] 9. compliance of test lung (QuickLung adjustable)
- [ ] 10. test lung (QuickLung)

zajdel, 2020-06-04:
Table 201.105 from ISO.80601-2-80-2018

| Test number | Intended delivered volume (mL) | Compliance (mL (hPa)^-1) | Linear resistance (hPa(L/s)^-1) +/- 10% | Leakage (mL/min) +/- 10% | Ventilatory frequency (breaths/min) | Inspiratory time (s) | Pressure (hPa) | PEEP (hPa) |
|-------------|--------------------------------|--------------------------|-----------------------------------------|--------------------------|-------------------------------------|----------------------|----------------|------------|
| 1           | 500                            | 50                       | 5                                       | 0                        | 20                                  | 1                    | 10             | 5          |
| 2           | 500                            | 50                       | 20                                      | 0                        | 12                                  | 1                    | 15             | 10         |
| 3           | 500                            | 20                       | 5                                       | 0                        | 20                                  | 1                    | 25             | 5          |
| 4           | 500                            | 20                       | 20                                      | 0                        | 20                                  | 1                    | 25             | 10         |
| 5           | 500                            | 50                       | 5                                       | 5000                     | 20                                  | 1                    | 25             | 5          |
| 6           | 500                            | 50                       | 20                                      | 10000                    | 12                                  | 1                    | 25             | 10         |
| 7           | 300                            | 20                       | 20                                      | 0                        | 20                                  | 1                    | 15             | 5          |
| 8           | 300                            | 20                       | 50                                      | 0                        | 12                                  | 1                    | 25             | 10         |
| 9           | 300                            | 10                       | 50                                      | 0                        | 20                                  | 1                    | 30             | 5          |
| 10          | 300                            | 20                       | 20                                      | 3000                     | 20                                  | 1                    | 25             | 5          |
| 11          | 300                            | 20                       | 50                                      | 6000                     | 12                                  | 1                    | 25             | 10         |
| 12          | 200                            | 10                       | 20                                      | 0                        | 20                                  | 1                    | 25             | 10         |

Notes:
- Volume in column 2 is intended to be used for selection of the test conditions and parameters based on the intended delivered volume of Ventilator Support Equipment (what does this mean?)
- For the purpose of this test, VSB is set up with artificial leakage (column 4) at a constant pressure of 20 hPa
- In the case that end-expiratory flow does not reach zero, reduce the ventilatory frequency (column 6) until it does for at least 50 ms
- The rise time of the ventilatory support equipment should be set to a value that ensures that the set pressure can be reached within the inspiratory time (i.e. 1 second in every case - your time to shine, Manuel!)
- For the purposes of this test, the set pressure is relative to set PEEP (that means =  PEEP + pressure? i.e. test number 1, we're looking for 15 hPa in our pressure readings?)

zajdel, 2020-06-04:
Section on pressure-controlled breath type (201.12.1.102)
- [ ]  a) If pressure-controlled breath type is provided, then with a pressure-controlled breath type selected and VSE operating in normal condition, the accuracy as determined for the test settings and conditoins specified shall be disclosed as the maximum bias error and maximum linearity error (example: +/- 3.0 + (5% of the set pressure)) hPa)
- [ ] b) This disclosure includes at least
       1) maximum error of airway pressure (Paw) at end of inspiratory phase in relation to set value
       2) maximum error of airway pressure (Paw) at the end of the inspiratory phase in relation to the set value under leak condition
       3) maximum error of airway pressure (Paw) at end of expiratory phase in relation to set value
       4) maximum error of airway pressure (Paw) at end of expiratory phase in relation to set value under leak condition
- [ ] c) All of the errors may be separately reported for the following ranges of intended delivered volume:
       1) Vdel >= 300 mL
       2) 300 mL >= Vdel >= 50 mL
- [ ] d) The accuracy of the performance of the ventilatory support equipment shall either be:
       1) determined for each VBS configuration indicated in the instructions for use; or
       2) determined for the worst-case VBS configuration indicated in the instructions for use (NOTE 1: The worst-case VBS configuration can be different for each error or each nominal delivered volume range)
- [ ] e) If worst-case VBS configurations are used, the rationale for their selection shall be documented in the *risk management file*

_Check compliance by inspection of the *risk management file* for the rationale, if applicable, and with the following tests for end-inspiratory and end-expiratory pressure errors:_
- [ ] f) Set up the ventilatory support equipment as shown in Figure 201.101 (above)
- [ ] g) If applicable, determine or input the VBS compliance required for compliance correction as indicated in the instructions for use and activate this correction. If a humidifier is used, fill the humidifier to the maximum water level prior to determining the VBS compliance.
- [ ] h) Utilize the rest parameters of the first applicable row (selected by typical intended delivered volume) of Table 201.105. Wait until steady-state conditions are achieved.
- [ ] i) Determine the airway pressure (Paw) at the end of the inspiratory phase as the average over the preceding 50 ms
- [ ] j) Compare the result with the pressure setting for the test. Confirm that the resulting difference is within the tolerance indicated in the instructions for use.
- [ ] k) Determine the PEEP as the averages of the airway pressure measurements (Paw) over the last 50 ms of the expiratory phase
- [ ] l) Compare the result with the PEEP setting for the test. Confirm that the resulting difference is within the tolerance indicated in the instructions for use.
- [ ] m) Repeat g) to l) for 30 consecutive breaths
- [ ] n) Repeat g) to m) for each applicable row (selected by intended delivered volume) of Table 201.105
- [ ] o) If a humidifier is included in the VBS, repeat the airway pressure tests with the minimum humidifier water level without re-determining the VBS compliance
- [ ] p) If the ventilatory support equipment permits operation without compliance correction, repeat g) to o) without compliance correction.
- [ ] q) Compare each result to the tolerance indicated in the instructions for use.

zajdel, 2020-06-04:
Main takeaways for now:
- Instructions for use keep popping up. Our test results will have to corroborate with the instructions for use.
- We seem to need to disclose 4 maximum errors, all for the airway pressure: Inspiratory phase, Inspiratory phase + leak, Expiratory phase, Expiratory phase + leak
- Are we allowing operation without VSB compliance correction? Seems we are required to allow operation with VSB compliance correction.
- What is our intended delivered volume for the ventilatory support equipment? Would we pick 500 mL (for adults?) and then go with tests 1-6? Are tests 7-12 applicable?
- We need to determine our steady state airway pressure, then average for 50 ms to get our test results both in PEEP and PIP phases. And we must do this for 30 cycles for each test condition.
- If we're using a humidifier, we have to do all tests twice: once at maximum humidifier water level and once at minimum humidifier water level.

CohenLabPrinceton, 2020-06-04:
@zajdel we do NOT need a temperature sensor for formal logging. That's actually excluded somewhere else in the EUA as irrelevant if we don't use a heated humidifier.

zajdel, 2020-06-04:
> 
> 
> @zajdel we do NOT need a temperature sensor for formal logging. That's actually excluded somewhere else in the EUA as irrelevant if we don't use a heated humidifier.

Since we are not using a heated humidifier, (g) part ii and (o) are not relevant. Also, we will not need to use a temperature sensor (component 6). These parts have been checked off.

Is the data acquisition system for test (component 5) to be separate/distinct from the ventilator itself (component 1)?

zajdel, 2020-06-04:
For component 8 in the test setup, pressure sensor, our Amphenol sensors (https://www.mouser.com/datasheet/2/18/1/DS-0103-Rev-A-1499253.pdf) have a response time to get to 90% pressure applied of < 100 microseconds.

juliennelachance, 2020-06-04:
The current read time is 2 ms per sensor. (So if you need to read more than one sensor, of course, it adds to the total time.)

juliennelachance, 2020-06-04:
Also: I am in favor of using the HME-F luer lock connector for now. So that takes care of checkboxes 2 and 5

closed 2020-10-06 by zajdel

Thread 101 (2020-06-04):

CohenLabPrinceton/pvp #101: TestReport: Airway Pressure Protection

CohenLabPrinceton, 2020-06-04:
Ref: ISO 80601-2-80 / 201.12.4.101.1

**General**

- [ ] a) The VENTILATORY SUPPORT EQUIPMENT shall be equipped with MONITORING EQUIPMENT to indicate the AIRWAY PRESSURE.

- [ ] b) The site of actual measurement may be anywhere in the VENTILATOR BREATHING SYSTEM, but the indicated value shall be referenced to the PATIENT‐CONNECTION PORT.

- [ ] c) Under steady‐state conditions, the indicated AIRWAY PRESSURE shall be accurate to within ± (2 + 4 % of the actual reading) hPa (cmH2O).

CohenLabPrinceton, 2020-06-04:
We need to confirm the error/accuracy of the pressure sensor. Do we have this in the spec sheet? How else should we quantify this?

juliennelachance, 2020-06-04:
The maximum linearity/hysteresis error at standard temperature is reported as +/- 0.5 %fs. Corresponding to a full-scale of 1 psi, this gives us an error of around 0.35 cm H20. 

Datasheet for reference: 
https://www.mouser.com/datasheet/2/18/1/DS-0103-Rev-A-1499253.pdf
We use the 1 PSI-D-4V-MINI as our system pressure sensor (with one side open to ambient).

zajdel, 2020-06-04:
Just to add to this, the nominal output voltage span is +/- 1.9 V to +/- 2.1 V. This could result in an error of up to 0.1 V / 2 V range (assumed) -> 0.05 psi or 3.5 cm H2O, worst case (5% off measured). We can easily calibrate the offset voltage (and should!), but may consider including an additional calibration procedure to measure the output span if this potential error must be reduced.

zajdel, 2020-06-09:
Our maximum error of +/- 3.5 hPa at full scale (1 psi = 70 hPa) is within the ± (2 + 4 % of the actual reading) hPa (cmH2O) requirement, even with the additional linearity error of 0.35 hPa that Julie cites, for a total error of +/- 3.85 hPa at full scale (our worst case). At full scale (70 hPa), we are allowed +/- 4.8 hPa error, according to the requirements.

I have checked the final box so this issue is pending closure.

CohenLabPrinceton, 2020-06-18:
@juliennelachance @zajdel please confirm the error statement.

closed 2020-10-09 by CohenLabPrinceton

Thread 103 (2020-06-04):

CohenLabPrinceton/pvp #103: TestReport: High-Airway Pressure Alarm -- the BIG ONE

CohenLabPrinceton, 2020-06-04:
- [ ] a) If the MAXIMUM LIMITED PRESSURE is greater than 40 hPa (40 cmH2O), the VENTILATORY SUPPORT EQUIPMENT shall be equipped with an ALARM SYSTEM that detects a high AIRWAY PRESSURE ALARMCONDITION to indicate when the high AIRWAY PRESSURE ALARM LIMIT is reached.

 b) The high AIRWAY PRESSURE ALARM CONDITION

- [ ] 1) shall be HIGH PRIORITY, unless

- [ ] 2) an INTELLIGENT ALARM SYSTEM, based on additional information, determines that

- [ ] i) the HIGH AIRWAY PRESSURE ALARM CONDITION is suppressed, or

- [ ] ii) its priority is changed.

c) The high AIRWAY PRESSURE ALARM LIMIT may be

- [ ] 1) independently adjustable,

- [ ] 2) connected to an adjustable pressure limitation, or

3) related to the set pressure of the VENTILATORY SUPPORT EQUIPMENT.

- [ ] d) If the high AIRWAY PRESSURE ALARM LIMIT is independently adjustable, it shall not be possible to set the ALARM LIMIT to a value less than that of the adjustable pressure limitation.

- [ ] e) PATIENT‐generated transient pressure increases should not cause the high AIRWAY PRESSURE ALARM CONDITION. EXAMPLE Transient pressure increase caused by the PATIENT coughing.

- [ ] f) The high AIRWAY PRESSURE ALARM CONDITION DELAY shall not exceed 200 ms and the VENTILATOR shall

- [ ] 1) act to attempt to cause the pressure to start to decline within that duration, and

- [ ] 2) act to prevent the pressure from continuing to rise.

g) Whenever the AIRWAY PRESSURE ALARM CONDITION occurs, the VENTILATOR shall, within no more than
two breath cycles or 15 s, whichever is less, reduce the AIRWAY PRESSURE to either:

- [ ] 1) atmospheric pressure, or

- [ ] 2) the set PEEP level.

- [ ] h) During SINGLE FAULT CONDITION, the AIRWAY PRESSURE may be reduced below the set PEEP level.

CohenLabPrinceton, 2020-06-04:
@sneakers-the-rat @mschottdorf Here's the BIG ONE. Let's make sure we're all on the same page here. Lemme know if we should meet to go over these. We also need test protocols to make sure these work.

sneakers-the-rat, 2020-06-22:
https://github.com/CohenLabPrinceton/Ventilator-Dev/blob/4c7c929df47941c2f3d7aad93c31c2311e44b339/vent/alarm/__init__.py#L77

a) does this say that the alarm should only fire when PIP is set above 40? currently alarm fires whenever measured PIP is 15% above set PIP.

b) HAPA is always HIGH, and remains actively displayed until 
* the measured pip is below 15% above set pip 
AND
* the user manually acknowledges & dismisses the alarm. 

c) (3) - HAPA threshold is computed as 15% above set PIP

d) alarm threshold not independently adjustable

e) @mschottdorf is the controller doing some filtering on the PIP values you're sending up? It looks like an alarm gets created regardless of whether or not the cough duration is met, i think you might need to make a `tentative_hapa` alarm object and check on its start time before creating the actual `self.HAPA` that's gotten by `get_alarms`

f) controller creates HAPA as soon as out-of-bounds pressure is detected, GUI polls alarms continuously from controller and raises them as soon as it gets them. 

f1 + f2) @mschottdorf can comment on this. I think it should probably be changed to g2 (set PIP to PEEP) : https://github.com/CohenLabPrinceton/Ventilator-Dev/blob/296b47f3baf5d0d1179008bd833855163a06210d/vent/controller/control_module.py#L398

closed 2020-10-09 by CohenLabPrinceton

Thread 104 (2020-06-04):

CohenLabPrinceton/pvp #104: TestReport: Measurement of expired volume

CohenLabPrinceton, 2020-06-04:
- [ ] If VENTILATORY SUPPORT EQUIPMENT is equipped with MONITORING EQUIPMENT for indicating the volume expired through the PATIENT‐CONNECTION PORT, the accuracy shall be disclosed in the instructions for use.

We need to quantify the tidal volume accuracy. @SophieDvali ?

juliennelachance, 2020-06-04:
This is a good question for Sophie- who has the D-Lite data.

SophieDvali, 2020-06-04:
I can calculate this using the flow data from the mfc. This is asking for just the error in the flow right since the tidal volume is just flow times the expiration time?

SophieDvali, 2020-06-10:
When calculating just the error in the flow (from the dlite) I get a fractional error of around 5% which is reasonable and also consistent with what Philippe gets for the physics flow sensor. However, if I use error prop to get the error in the VT it becomes much higher (like 70%). I feel like there might be something wrong here.

closed 2020-10-09 by CohenLabPrinceton

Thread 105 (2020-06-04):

CohenLabPrinceton/pvp #105: TestReport: Max Limited Pressure Protection Device

CohenLabPrinceton, 2020-06-04:
MAXIMUM LIMITED PRESSURE PROTECTION DEVICE

- [ ] a) A PROTECTION DEVICE shall be provided to prevent the AIRWAY PRESSURE from exceeding the MAXIMUM LIMITED PRESSURE under both NORMAL CONDITION and SINGLE FAULT CONDITION.

- [ ] b) The MAXIMUM LIMITED PRESSURE shall not exceed 90 hPa (90 cmH2O)

@juliennelachance @zajdel @sneakers-the-rat let's confirm our max pressure limit in the software as well as the specs on our safety valves. Please disclose all relevant specs in the comments below @juliennelachance @zajdel

zajdel, 2020-06-04:
We have a physical pressure release valve that will limit pressure to ~69 hPa (1 psi), placed just at the output of the inspiratory valve. The valve specs: [](https://www.mcmaster.com/4277T52)

Stated accuracy of set pressure release is +/- 20%, so within tolerance, the pressure limit is 55-83 hPa.

@mschottdorf can confirm his implementation of a software-based max pressure limit.

mschottdorf, 2020-06-05:
There is a software-coded maximum pressure limit, yes, that overwrites controller instructions and opens the exp. valve, and closed the inspiratory valve.
 If the hardware-config-file is correct, it actually works quite well :-)

zajdel, 2020-06-05:
It sounds like we have this covered, but I would like clarification on what the "single fault condition" is. We do limit pressure in two redundant ways during "normal operation." Does "single fault" simply mean that one component is not operating as desired?

CohenLabPrinceton, 2020-06-12:
@zajdel single fault condition means if if a key component fails (just one).

closed 2020-06-12 by CohenLabPrinceton

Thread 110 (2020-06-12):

CohenLabPrinceton/pvp #110: TestReport: High Leakage Alarm

CohenLabPrinceton, 2020-06-12:
- [ ] a) The VENTILATORY SUPPORT EQUIPMENT may be equipped with an ALARM SYSTEM that detects a TECHNICALALARM CONDITION to indicate when conditions in the VBS reach the ALARM LIMIT for high leakage.

- [ ] b) If provided, the high leakage TECHNICAL ALARM CONDITION shall be at least MEDIUM PRIORITY, unless an INTELLIGENT ALARM SYSTEM, based on additional information, determines that the high leakage TECHNICAL ALARM CONDITION is suppressed, or its priority is changed

CohenLabPrinceton, 2020-06-12:
@mschottdorf @sneakers-the-rat need to confirm leakage alarm exists and works.

sneakers-the-rat, 2020-06-22:
Tell me how to parameterize leak and i'll implement in alarm manager.

CohenLabPrinceton, 2020-06-22:
@mschottdorf @zajdel we need to think about how the controller knows when there is a leak. Normally that would be handled by mass conservation with dual flow sensors, but we need an alternative. Might be issues with rise time, or maintaining pressure, etc.

closed 2020-10-09 by CohenLabPrinceton

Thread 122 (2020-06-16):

CohenLabPrinceton/pvp #122: TestReport: Anti-suffocation testing

CohenLabPrinceton, 2020-06-16:
- [ ] c) Under these conditions, the inspiratory and expiratory pressure drop measured at the PATIENT-CONNECTION PORT with all recommended ACCESSORIES in place shall not exceed 6,0 hPa (6,0 cmH2O) at a flowrate of:

- [ ] 1) 30 l/min for VENTILATORY SUPPORT EQUIPMENT intended to provide a DELIVERED VOLUME, Vdel ≥ 300 ml;

- [ ] 2) 15 l/min for VENTILATORY SUPPORT EQUIPMENT intended to provide a DELIVERED VOLUME, Vdel ≤ 300 ml;

CohenLabPrinceton, 2020-06-16:
Need to make sure about the pressure drop when ALL of our HEPA and HMEF etc. are installed. How do we test this? @juliennelachance @zajdel @SophieDvali

juliennelachance, 2020-06-16:
We'll need to measure pressure at the inspiratory and expiratory connections. Maybe Tom can use one of our old 3d printed pressure take-off pieces to take the inspiratory pressure reading. Then the expiratory reading will come from the D-Lite as usual

CohenLabPrinceton, 2020-06-22:
@juliennelachance @zajdel I think this needs to be tested just at the proximal port. We need to measure the pressure drop during inspiration to get to the patient and the pressure drop from the patient to the exp valve essentially.

CohenLabPrinceton, 2020-10-09:
Closing all TestReport issues for cleanup

closed 2020-10-09 by CohenLabPrinceton

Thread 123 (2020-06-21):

CohenLabPrinceton/pvp #123: Optimizing PID control coefficients and performance

mschottdorf, 2020-06-21:
This is to track progress on the dinky, and find the optimal settings to control hardware.

zajdel, 2020-06-21:
Main concern right now is that setting the pressure upstream of the prop valve may not be giving us a high enough flow rate to inflate the lung within 0.2-0.3 seconds, regardless of PIP setting.

CohenLabPrinceton, 2020-06-21:
@mschottdorf @zajdel can you put some waveforms up? Does this depend at all on the inspiratory time setting?

zajdel, 2020-06-24:
Significant progress achieved by using gain scheduling to account for the delay in the pressure propagation. Committed, but not pushed yet. I think I just need to be given push access to manuel's fork.

zajdel, 2020-06-24:
[image]

Showing results from test condition 4 (compliance: 20, resistance: 20, PIP: 35, PEEP: 10)

mschottdorf, 2020-06-24:
I'll implement djc's matlab export, fix J's issues with the PR, then merge your stuff, and we are good :-)

mschottdorf, 2020-10-09:
also done!

closed 2020-10-09 by mschottdorf

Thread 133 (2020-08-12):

CohenLabPrinceton/pvp #133: HAPA correction in controller overwritten

sneakers-the-rat, 2020-08-12:
I'm debugging the erratic_dt controller test and I noticed something weird, I kept getting HAPA warnings, but the set PIP remained at its default 35. When Pressure goes above the hapa_limit (initialized from default values, but updated from alarm_manager in normal usage) for a time longer than cough_duration, the Controller should set valves to close immediately and change the set PIP to 30:

https://github.com/CohenLabPrinceton/pvp/blob/a4d46449d1bf73e465314e4172f2edeb0062c512/pvp/controller/control_module.py#L500

the alarm test method is called inside the PID update method all inside the mainloop method. Later in the mainloop method, however, a check for updated controls happens that causes the `__SET_PIP` to be overridden:

https://github.com/CohenLabPrinceton/pvp/blob/a4d46449d1bf73e465314e4172f2edeb0062c512/pvp/controller/control_module.py#L913

Since the default number of control loops between those updates is 1, and `COPY_SET_PIP` is never changed by the alarm checking routine, the setting never takes effect.

I'm submitting a commit now to fix that part by just also changing `COPY_SET_PIP`, but i'm also concerned about what happens in the next iteration of the mainloop and don't know enough about how it works to confidently debug it: if PIP is set to 30, but there is still a high pressure problem, then we would be causing a high pressure problem on every breath cycle, correct? It seems to me like `__SET_PIP` should be decremented rather than set to a fixed value -- eg. what if `__SET_PIP` was lower than 30 but there was some other malfunction in the machine? And given the new design of the controller with the gain parameter, shouldn't the gain parameter be decremented as well?

sneakers-the-rat, 2020-08-12:
did the `COPY_SET_PIP` write in this commit https://github.com/CohenLabPrinceton/pvp/commit/57dc87e13b34b5e38f9289ff3f5e51f78e8b1374

mschottdorf, 2020-08-13:
Hm, the logic of the old thing was: if HAPA, open the exp. valve and close the insp. valve as soon as possible to reduce the excess pressure, and continue with hardcoded PIP of 30. In principle, PIP to 30 could be removed. 

The only really important thing about HAPA is to close inspiration & open expiration to reach a safe pressure. Once that is done, usual cycling should (even has to?) commence. I felt that resetting _all_ parameters to defaults might be a bit too much, so I touched only the PIP setting. Gain could also be reduced, I guess.

mschottdorf, 2020-09-05:
has beed removed; and HAPA algorithm simplified

closed 2020-09-05 by mschottdorf

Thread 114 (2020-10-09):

### ISSUE TITLE
Independence of ventilation control and risk control

### ISSUE THREAD

**Issue by CohenLabPrinceton** [CohenLabPrinceton/pvp#114]
a) A SINGLE FAULT CONDITION shall not cause the simultaneous failure of:

- [ ] 1) the ventilation‐control function; and

- [ ] 2) the corresponding PROTECTION DEVICE.

b) A SINGLE FAULT CONDITION shall not cause failure in such a way that a failure of:

- [ ] 1) the ventilation‐control function and the corresponding MONITORING EQUIPMENT is not detected,
or

- [ ] 2) the ventilation‐control function and the corresponding ALARM SYSTEM is not detected

**Comment by sneakers-the-rat** [comment]
need to know what 
* SINGLE FAULT CONDITION, 
* 'ventilation-control function', 
* 'PROTECTION DEVICE', and 
* 'MONITORING EQUIPMENT' 
mean to answer this

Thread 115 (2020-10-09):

### ISSUE TITLE
TestReport: Programmable Electrical Medical Systems (PEMS)

### ISSUE THREAD

**Issue by CohenLabPrinceton** [CohenLabPrinceton/pvp#115]
- [ ] Indicate whether the software was developed under a controlled life cycle process (e.g. IEC 62304 Medical device software — Software life cycle processes).   List any known unresolved software anomalies and workarounds.

**Comment by CohenLabPrinceton** [comment]
We don't need to use 62304, but we should discuss this fairly.

**Comment by sneakers-the-rat** [comment]
not sure what's required here, unfamiliar with 'controlled life cycle processes.' if this could get juiced out into specific questions i can answer them. seems like 'how did we go about planning development?'

**Comment by mschottdorf** [comment]
- Current software-anomaly: glitches from the hardware sensors.

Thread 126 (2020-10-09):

### ISSUE TITLE
Flow: Fix the GUI, fix the calibration

### ISSUE THREAD

**Issue by CohenLabPrinceton** [CohenLabPrinceton/pvp#126]
- [ ] Tidal Volumes calculation and display needs to be correct

- [x] LPM not LPS for flow

- [ ] @juliennelachance will follow up with @SophieDvali 

- [ ] Revised interface

**Comment by sneakers-the-rat** [comment]
what does 'revised interface' mean?

**Comment by sneakers-the-rat** [comment]
displayed units are now correct (L/min rather than l/s) https://github.com/CohenLabPrinceton/Ventilator-Dev/pull/127/commits/55a48cf19c2679f4548f0144dd8e34a08bfeac3b#

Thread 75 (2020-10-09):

### ISSUE TITLE
List of good features

### ISSUE THREAD

**Issue by sneakers-the-rat** [CohenLabPrinceton/pvp#75]
Let's start braggin.  What do we do well? Comment i'll keep this list updated

## Software as a whole

1. Is super fast. No problems with PID and 10ms loop time. If we find the time, we should measure how fast we actually are.

2. Very limited load on the PI. With 10ms loop time, controlling the dinky through ssh w/o UI is ~25% CPU load and 5% memory.

## GUI

- ay we have one
- Modularly designed with widely-used open-source GUI framework (Qt, PySide2)
- etc. jonny will fill out

## Alarms

- Flexible but inspectable alarm declaration syntax
- etc. jonny will fill out

## Controller

1. We support two control schemes, PID and state control. These are very simple to adjust should the need arise, and particularly flexible for adjustment to specific needs. For example, if PEEP valves become unobtanium, the PID-loop can actively control PEEP.

2. The Controller is concise, modular, subject to a well-documented API, and fully open source. This makes it much easier to find, and fix, bugs.

3. Its modularity makes it easy to re-use the Controller with a different, or remote, UI.

4. Rigorous exception handling and careful time-outs make sure that the program as a whole remains operational.

**Comment by mschottdorf** [comment]
To the point of [PEEP valve] vs. [PID control of PEEP]. This works really well:

![image](https://user-images.githubusercontent.com/3635994/84055406-c5f17600-a982-11ea-8b73-bb8c5445c849.png)

Can be adjusted in the main controller loop with `PEEP_VALVE_SET = True`.

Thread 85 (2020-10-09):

### ISSUE TITLE
TestReport: Compliance with IEC 60601-1 sec. 5 for testing

### ISSUE THREAD

**Issue by ProfDJCohen** [CohenLabPrinceton/pvp#85]
This is a hard one. We need to certify to the best of our ability a variety of things about how testing is conducted. In some cases, we cannot do this (we do not have a synthetic 'finger' with a force sensor that we can use to test 'finger poking' resistance, for instance). 

We may also need to do a humidity test. I need eyes on this and feedback. 

We need serious advice on this. 
[IEC-60601-1-s5.pdf](https://github.com/CohenLabPrinceton/Ventilator-Dev/files/4723642/IEC-60601-1-s5.pdf)

**Comment by CohenLabPrinceton** [comment]
Need to talk to consultants about how to handle this? Say "not evaluated"?

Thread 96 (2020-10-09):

### ISSUE TITLE
TestReport: Biocompatibility Report

### ISSUE THREAD

**Issue by CohenLabPrinceton** [CohenLabPrinceton/pvp#96]
This has been strongly stripped down from the normal approach:

BIOCOMPATIBILITY of ME EQUIPMENT and ME SYSTEMS

`Provide a list of the materials used in the air path components`

![image](https://user-images.githubusercontent.com/56199891/83686124-b0153700-a5b7-11ea-9d9a-577e29c749b9.png)

**Comment by juliennelachance** [comment]
I went through the air pathway components. Not sure what all the medical-specific parts are made out of, but the spreadsheet is here:

https://docs.google.com/spreadsheets/d/1iNjTeL1b5Wdo9fmQ-OFB4NY6Sc-0JzTLDYsgRpo8cxQ/edit?usp=sharing

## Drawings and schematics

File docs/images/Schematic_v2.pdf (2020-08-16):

# PVP1

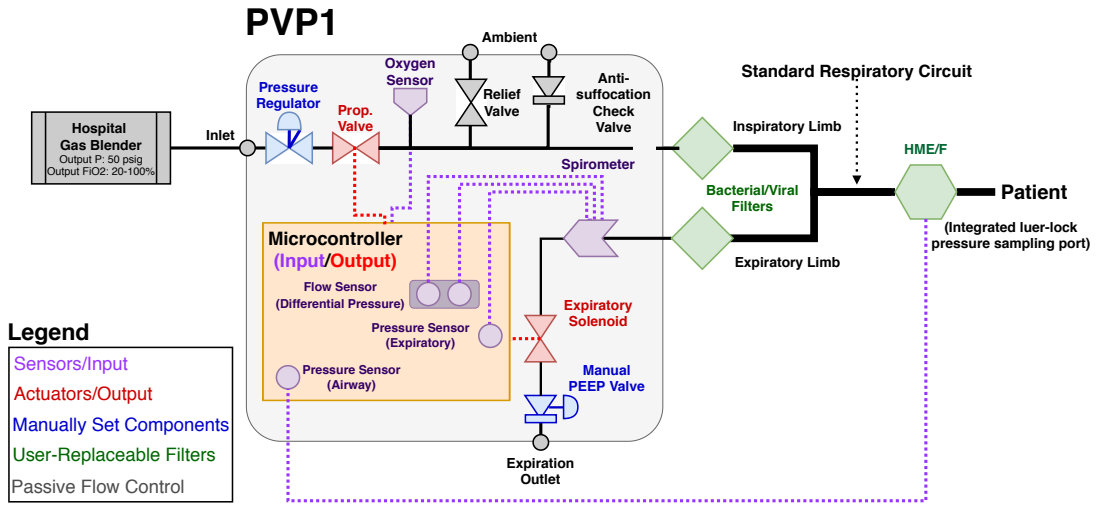
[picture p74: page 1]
Hospital Gas Blender Output P: 50 psig Output FiO2: 20-100%; Prop. Valve; Pressure Regulator; Oxygen Sensor; Relief Valve; Expiratory Solenoid; Anti- suffocation Check Valve; Ambient; Expiration Outlet; Bacterial/Viral Filters; HME/F; Flow Sensor (Differential Pressure); Pressure Sensor (Airway); Microcontroller (Input/Output); Inlet; Inspiratory Limb; Expiratory Limb; Patient; Manual PEEP Valve; Spirometer; Pressure Sensor (Expiratory)

Standard Respiratory Circuit

(Integrated luer-lock
pressure sampling port)

Legend
Sensors/Input
Actuators/Output
Manually Set Components
User-Replaceable Filters
Passive Flow Control

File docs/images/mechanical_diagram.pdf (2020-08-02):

# Inspiratory

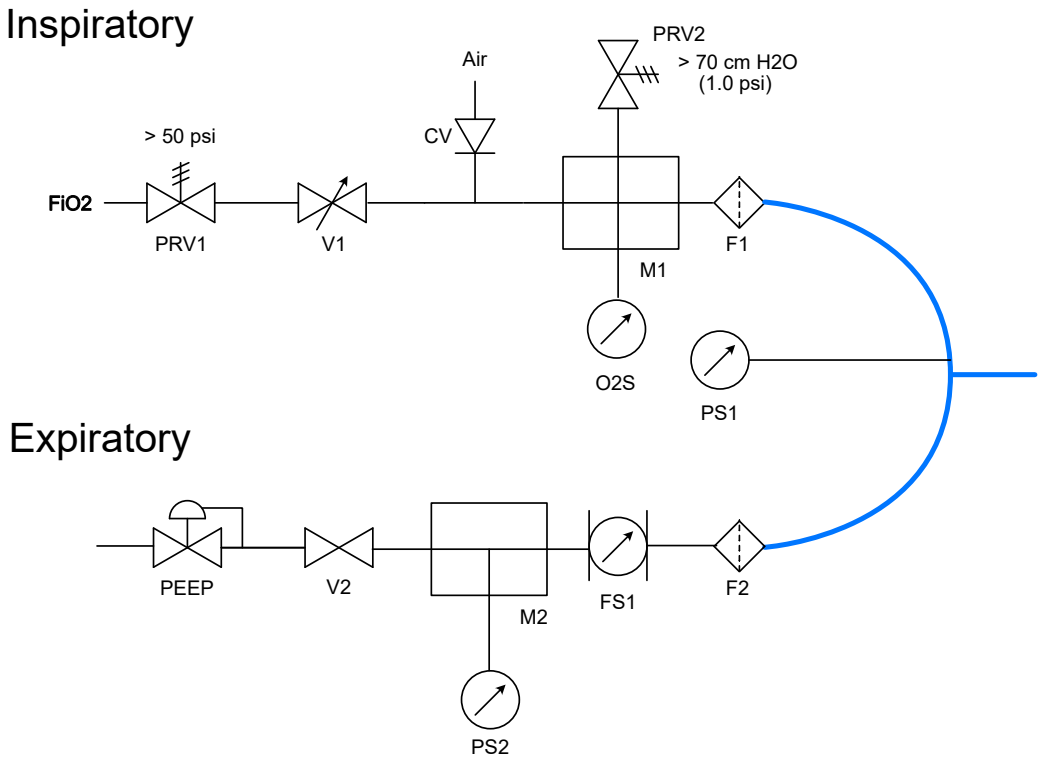
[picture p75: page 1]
> 50 psi; PRV1; PRV2 > 70 cm H2O (1.0 psi); Expiratory; PEEP; Air; FiO2

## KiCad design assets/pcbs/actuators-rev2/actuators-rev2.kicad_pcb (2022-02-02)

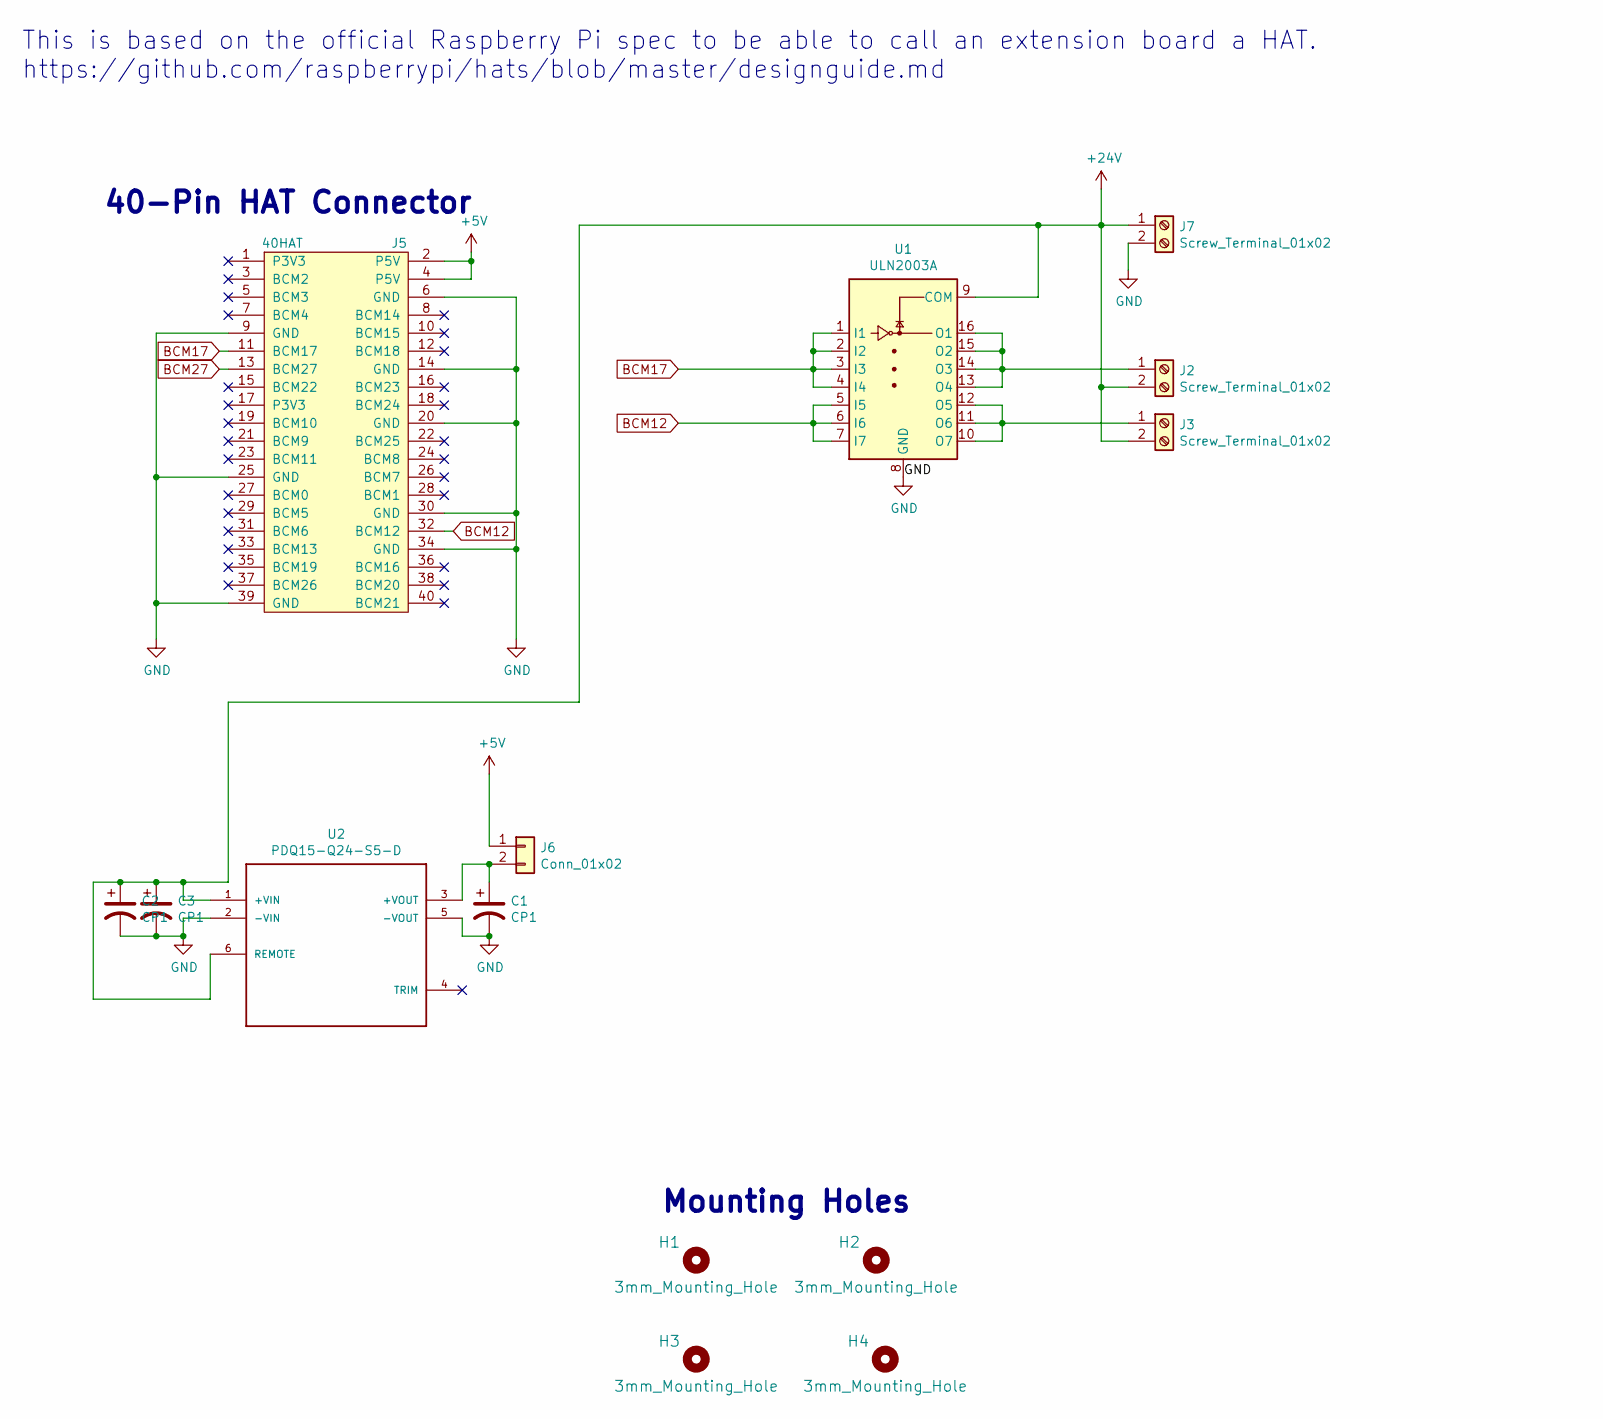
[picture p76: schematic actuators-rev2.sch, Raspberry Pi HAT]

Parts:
C1: CP1; CP_Radial_D5.0mm_P2.00mm
C2, C3: CP1; CP_Radial_D5.0mm_P2.50mm
H1, H2, H3, H4: 3mm_Mounting_Hole; NPTH_3mm_ID
J2, J3, J7: Screw_Terminal_01x02; TerminalBlock_Altech_AK300-2_P5.00mm
J5: 40HAT; PinSocket_2x20_P2.54mm_Vertical
J6: Conn_01x02; PinHeader_1x02_P2.54mm_Vertical
U1: ULN2003A; DIP-16_W7.62mm
U2: PDQ15-Q24-S5-D; CONV_PDQ15-Q24-S5-D

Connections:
+5V: J5.2 (P5V), J5.4 (P5V), J6.1
+24V: C2.1, C3.1, J2.2, J3.2, J7.1, U1.9 (COM), U2.1 (+VIN), U2.6 (REMOTE)
BCM12: J5.32 (BCM12), U1.5 (I5), U1.6 (I6), U1.7 (I7)
BCM17: J5.11 (BCM17), U1.1 (I1), U1.2 (I2), U1.3 (I3), U1.4 (I4)
BCM27: J5.13 (BCM27)
GND: C1.2, C2.2, C3.2, J5.6 (GND), J5.9 (GND), J5.14 (GND), J5.20 (GND), J5.25 (GND), J5.30 (GND), J5.34 (GND), J5.39 (GND), J7.2, U1.8 (GND), U2.2 (-VIN), U2.5 (-VOUT)
unnamed: C1.1, J6.2, U2.3 (+VOUT)
unnamed: J2.1, U1.13 (O4), U1.14 (O3), U1.15 (O2), U1.16 (O1)
unnamed: J3.1, U1.10 (O7), U1.11 (O6), U1.12 (O5)

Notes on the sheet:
Mounting Holes
40-Pin HAT Connector
This is based on the official Raspberry Pi spec to be able to call an extension board a HAT. https://github.com/raspberrypi/hats/blob/master/designguide.md

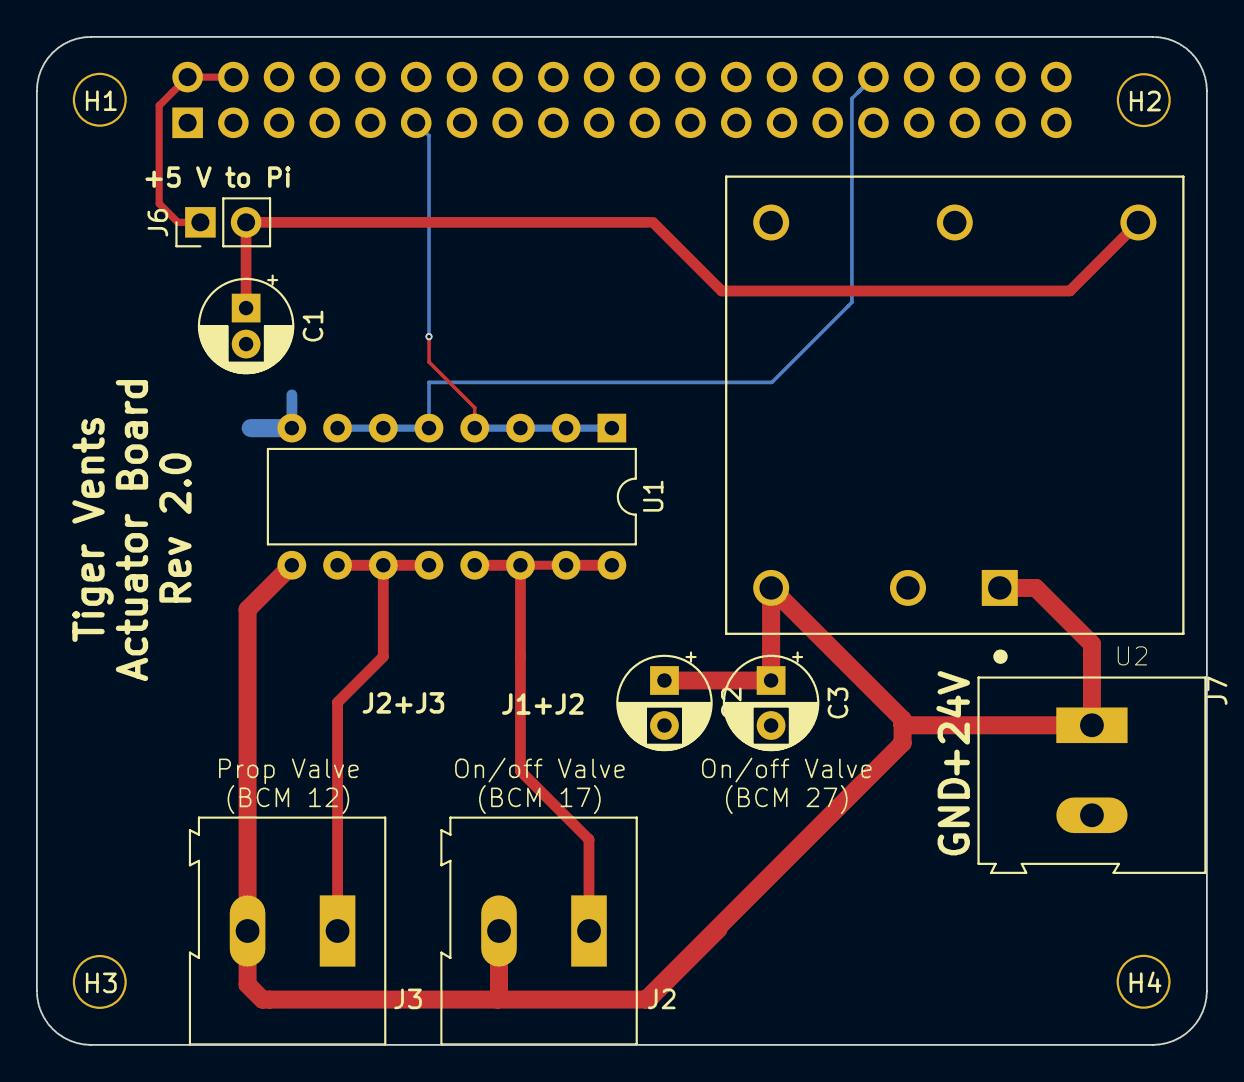
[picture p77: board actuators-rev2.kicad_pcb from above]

Board: 4 copper layers, 65.0 x 56.0 mm, 14 parts (1 on the bottom side), 8 nets.

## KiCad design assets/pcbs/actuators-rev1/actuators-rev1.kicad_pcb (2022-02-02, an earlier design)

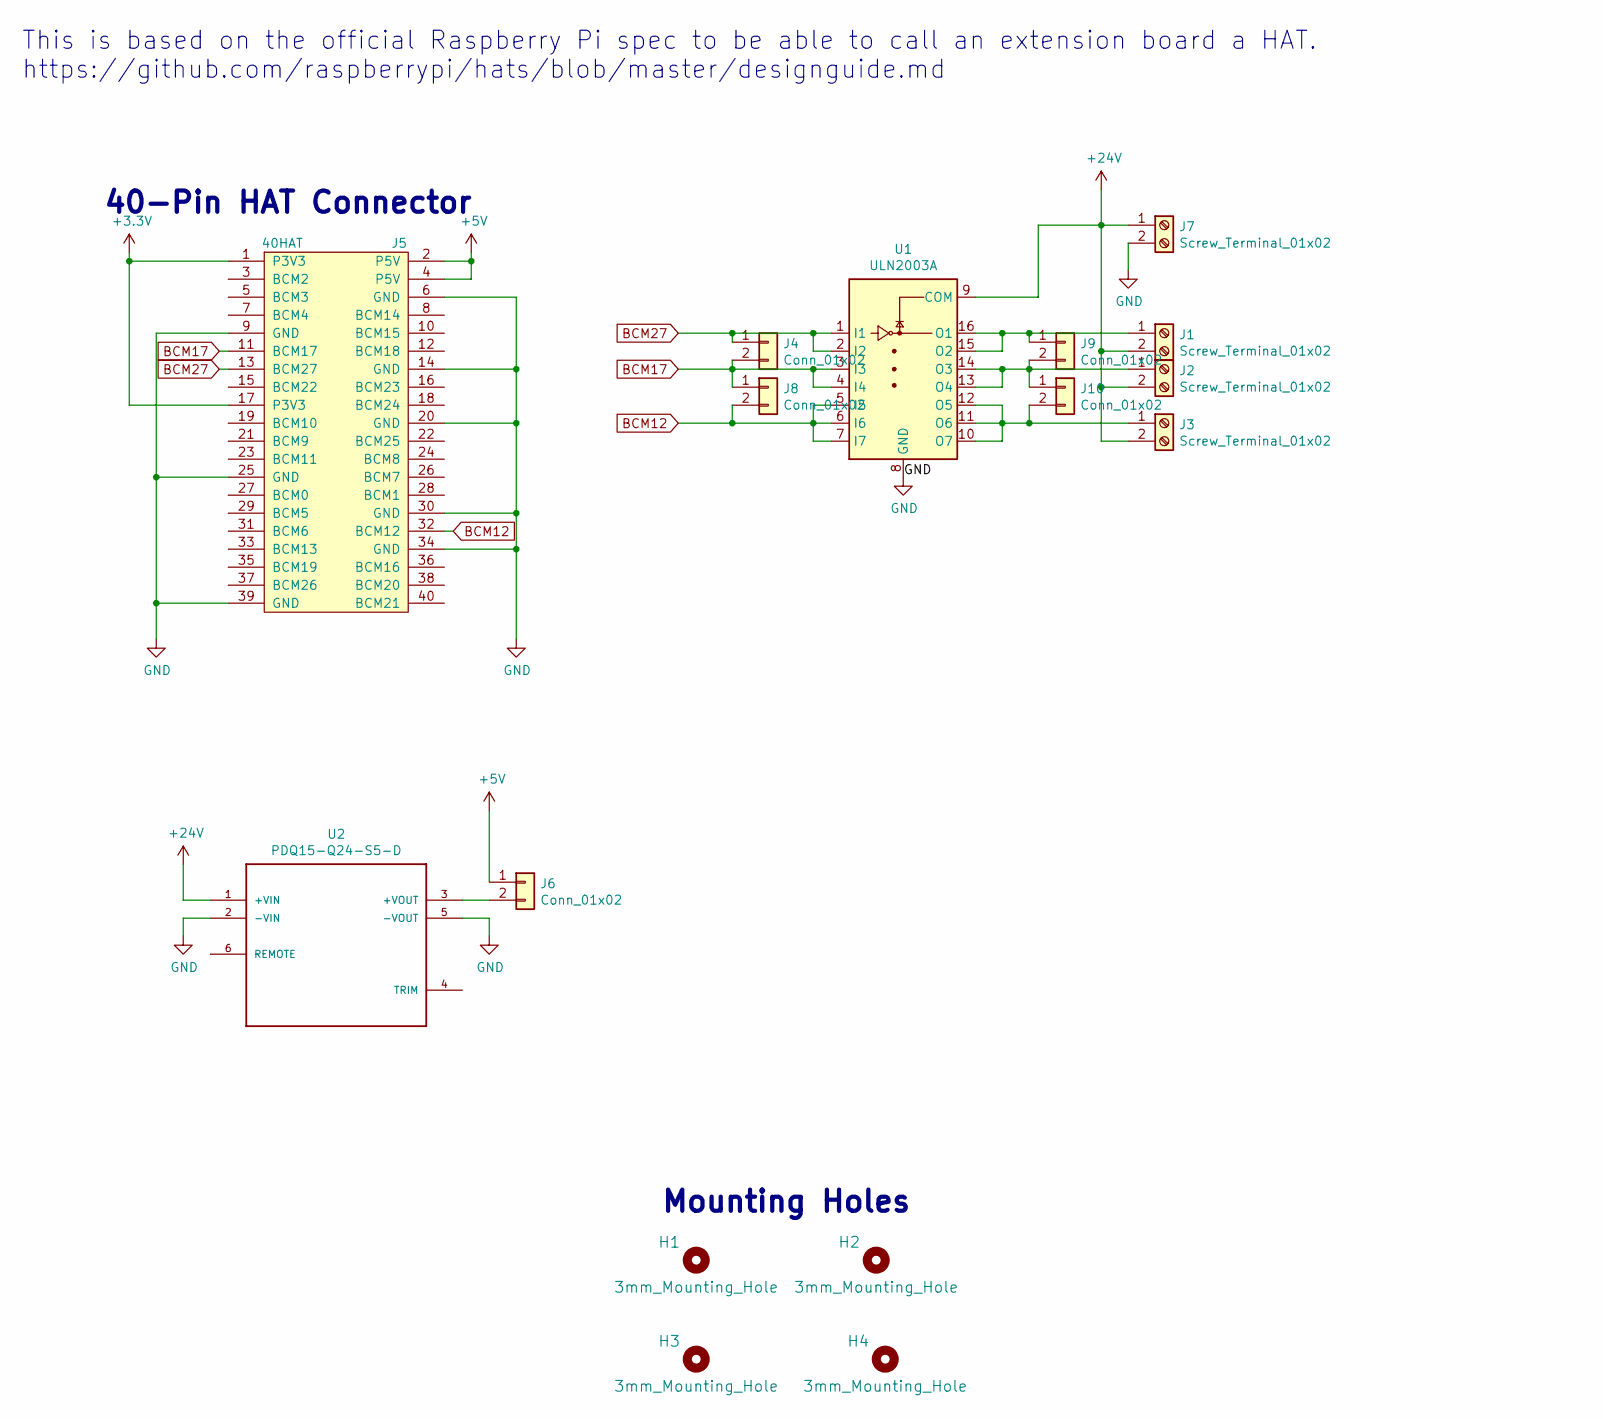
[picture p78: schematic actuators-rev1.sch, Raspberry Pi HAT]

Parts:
H1, H2, H3, H4: 3mm_Mounting_Hole; NPTH_3mm_ID
J1, J2, J3, J7: Screw_Terminal_01x02; TerminalBlock_Altech_AK300-2_P5.00mm
J4, J6, J8, J9, J10: Conn_01x02; PinHeader_1x02_P2.54mm_Vertical
J5: 40HAT; PinSocket_2x20_P2.54mm_Vertical
U1: ULN2003A; DIP-16_W7.62mm
U2: PDQ15-Q24-S5-D; CONV_PDQ15-Q24-S5-D

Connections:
+3V3: J5.1 (P3V3), J5.17 (P3V3)
+5V: J5.2 (P5V), J5.4 (P5V), J6.1
+24V: J1.2, J2.2, J3.2, J7.1, U1.9 (COM), U2.1 (+VIN)
BCM12: J5.32 (BCM12), J8.2, U1.5 (I5), U1.6 (I6), U1.7 (I7)
BCM17: J4.2, J5.11 (BCM17), J8.1, U1.3 (I3), U1.4 (I4)
BCM27: J4.1, J5.13 (BCM27), U1.1 (I1), U1.2 (I2)
GND: J5.6 (GND), J5.9 (GND), J5.14 (GND), J5.20 (GND), J5.25 (GND), J5.30 (GND), J5.34 (GND), J5.39 (GND), J7.2, U1.8 (GND), U2.2 (-VIN), U2.5 (-VOUT)
unnamed: J1.1, J9.1, U1.15 (O2), U1.16 (O1)
unnamed: J6.2, U2.3 (+VOUT)
unnamed: J2.1, J9.2, J10.1, U1.13 (O4), U1.14 (O3)
unnamed: J3.1, J10.2, U1.10 (O7), U1.11 (O6), U1.12 (O5)

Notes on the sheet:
Mounting Holes
40-Pin HAT Connector
This is based on the official Raspberry Pi spec to be able to call an extension board a HAT. https://github.com/raspberrypi/hats/blob/master/designguide.md

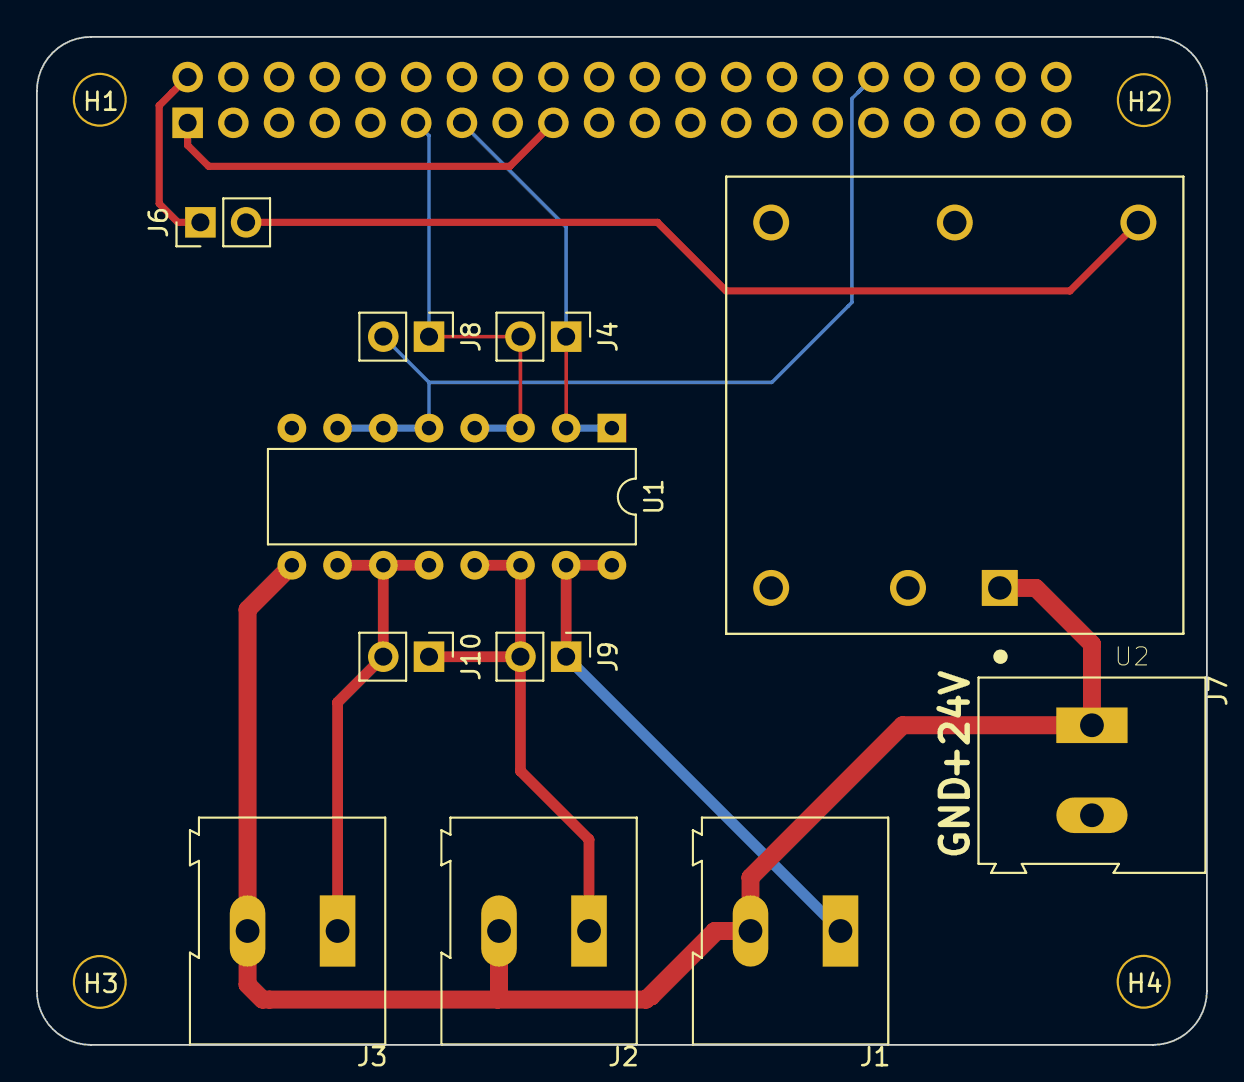
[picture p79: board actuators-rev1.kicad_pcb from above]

Board: 4 copper layers, 65.0 x 56.0 mm, 16 parts (1 on the bottom side), 11 nets.

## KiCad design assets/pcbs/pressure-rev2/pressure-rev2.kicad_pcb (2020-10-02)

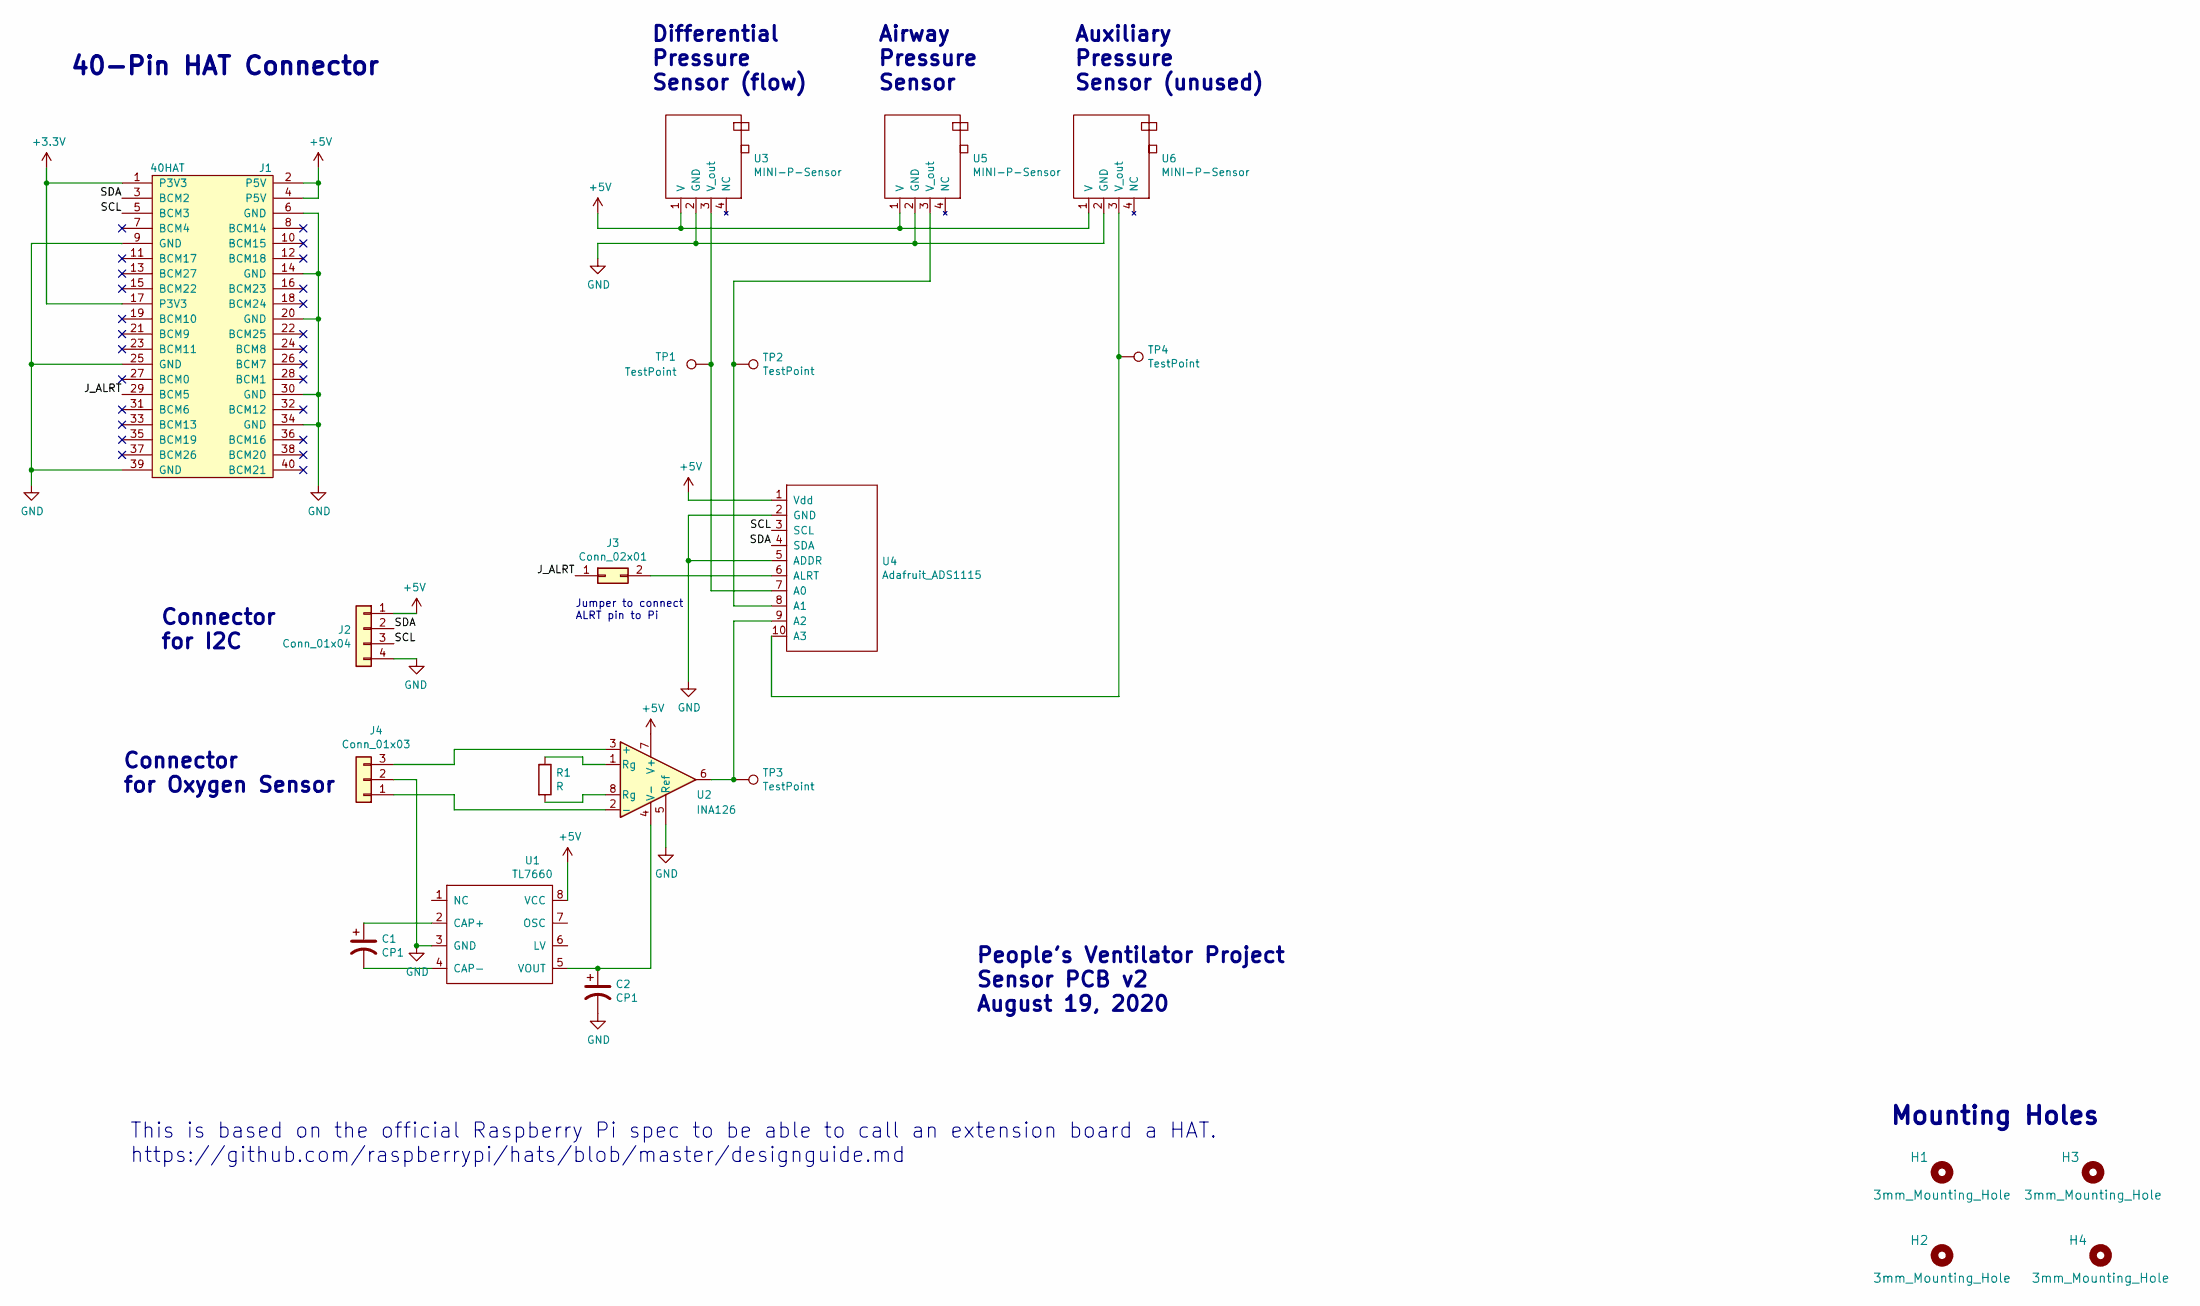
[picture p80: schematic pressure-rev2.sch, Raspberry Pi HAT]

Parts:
C1, C2: CP1; CP_Radial_D4.0mm_P2.00mm
H1, H2, H3, H4: 3mm_Mounting_Hole; NPTH_3mm_ID
J1: 40HAT; PinSocket_2x20_P2.54mm_Vertical
J2: Conn_01x04; PinHeader_1x04_P2.54mm_Vertical
J3: Conn_02x01; PinHeader_2x01_P2.54mm_Vertical
J4: Conn_01x03; PinHeader_1x03_P2.54mm_Vertical
R1: R; R_Axial_DIN0207_L6.3mm_D2.5mm_P10.16mm_Horizontal
TP1, TP2, TP3, TP4: TestPoint; TestPoint_THTPad_2.0x2.0mm_Drill1.0mm
U1: TL7660; DIP-8_W7.62mm
U2: INA126; DIP-8_W7.62mm
U3, U5, U6: MINI-P-Sensor; MINI-P-Sensor-Horizontal
U4: Adafruit_ADS1115

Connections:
+3V3: J1.1 (P3V3), J1.17 (P3V3)
+5V: J1.2 (P5V), J1.4 (P5V), J2.1, U1.8 (VCC), U2.7 (V+), U3.1 (V), U4.1 (Vdd), U5.1 (V), U6.1 (V)
/J_ALRT: J1.29 (BCM5), J3.1
/SCL: J1.5 (BCM3), J2.3, U4.3 (SCL)
/SDA: J1.3 (BCM2), J2.2, U4.4 (SDA)
GND: C2.2, J1.6 (GND), J1.9 (GND), J1.14 (GND), J1.20 (GND), J1.25 (GND), J1.30 (GND), J1.34 (GND), J1.39 (GND), J2.4, J4.2, U1.3 (GND), U2.5 (Ref), U3.2 (GND), U4.2 (GND), U4.5 (ADDR), U5.2 (GND), U6.2 (GND)
unnamed: C1.1, U1.2 (CAP+)
unnamed: C1.2, U1.4 (CAP-)
unnamed: C2.1, U1.5 (VOUT), U2.4 (V-)
unnamed: J3.2, U4.6 (ALRT)
unnamed: J4.1, U2.2 (-)
unnamed: J4.3, U2.3 (+)
unnamed: R1.1, U2.1 (Rg)
unnamed: R1.2, U2.8 (Rg)
unnamed: TP1.1, U3.3 (V_out), U4.7 (A0)
unnamed: TP2.1, U4.8 (A1), U5.3 (V_out)
unnamed: TP3.1, U2.6, U4.9 (A2)
unnamed: TP4.1, U4.10 (A3), U6.3 (V_out)

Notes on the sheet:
Mounting Holes
40-Pin HAT Connector
This is based on the official Raspberry Pi spec to be able to call an extension board a HAT. https://github.com/raspberrypi/hats/blob/master/designguide.md
Connector for Oxygen Sensor
Connector for I2C
Jumper to connect ALRT pin to Pi
Airway Pressure Sensor
Differential Pressure Sensor (flow)
Auxiliary Pressure Sensor (unused)
People's Ventilator Project Sensor PCB v2 August 19, 2020

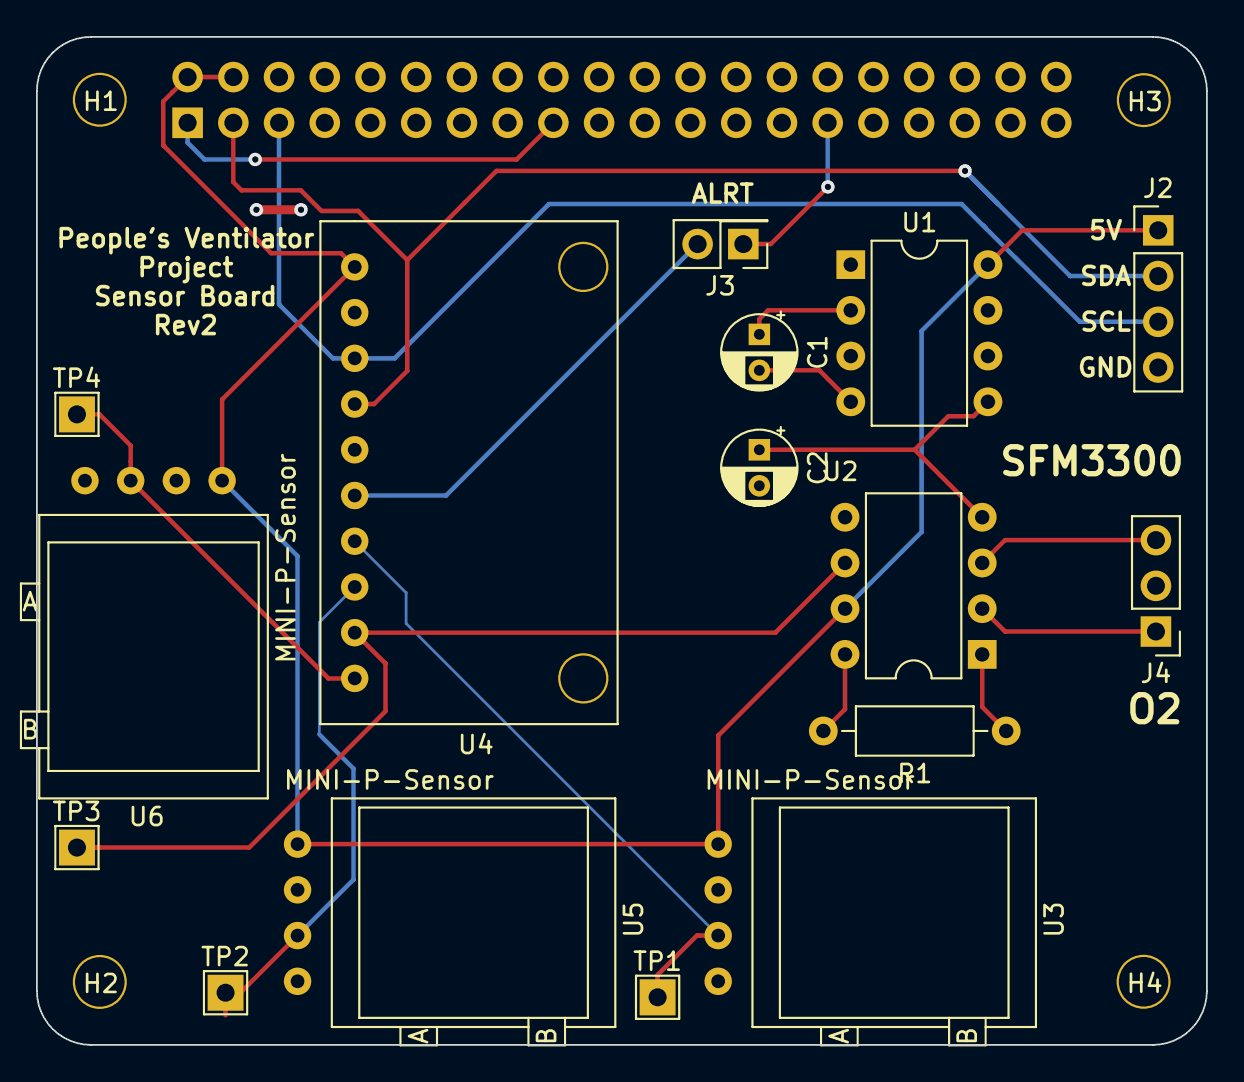
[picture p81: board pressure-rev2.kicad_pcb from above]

Board: 2 copper layers, 65.0 x 56.0 mm, 21 parts (1 on the bottom side), 18 nets.

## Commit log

2020-04-11 Implemented sensors through ADS1115
2020-04-14 Reworked structure of controls & sensors
2020-04-14 debug with physical testing of prototype
2020-04-15 Updated temperature sensor code
2020-04-15 Tweaked temperature display
2020-04-15 Cleaned up temp sensor interface
2020-04-17 refactor: rename gui_main as main, assuming this would be the entry of all program (local/remote, simulator/device)
2020-04-18 seems to work, threading wrapper is coded in the jupyter-notebook
2020-04-18 updated sensor values to include pressure updated the control class to return a well-formatted SensorValue instance
2020-04-18 seems to work well; updates to (1) messages.py for sensorvalues & controls, (2) control_module for the simple controller to work with leaky pipes and (3) notebook to demonstrate usage
2020-04-20 * refactor widgets into separate files * add threaded control_module to coordinator.control_module from sandbox example * eg. values.py
2020-04-22 feat: implement internal threading in Coordinator
2020-04-22 Control Module update to include threading
2020-04-22 update to notebook, cut out all the dead wood
2020-04-22 The contoller is now initialized with a main control thread and start() and stop() methods
2020-04-22 sensor values also return the loop counter - to be used as heart beat
2020-04-23 update with copies for threading
2020-04-24 updates for threading
2020-04-24 added to-do list for test - and cut out dead wood from notebook
2020-04-26 update and test for the heatbeat
2020-04-27 feat: thread-safe alarm functions
2020-04-29 changes per Grant's request. Set all the instance variables and then as the last thing the init does to start the thread.
2020-04-29 revised with hardware updates, a prop valve at inspiratory side, and open/close at expiratory side
2020-04-30 that was a proper bug in the PID controller. If the pressure has not reached PEEP, open up the valves.
2020-04-30 Refactored and tightened API. FIxed a bunch of bugs and probably added some more
2020-05-02 feat: define IPC on socket
2020-05-05 improved physics of the balloon simulator: (1) set and real values for flow in [Qin] and flow out [Qout] are now independent variables (2) Flow rates on the expiratory side are proportional to pressu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
2020-05-05 updates to balloon: flows only in the range of [0,2] l/sec updates to test: simulate with random update intervals anywhere between [0,100ms]
2020-05-06 Moved class definitions out of /vent/io/devices/__init__.py and into /vent/io/devices/base.py
2020-05-09 updated the notebook, and fixed the test for controller (screwed that up in the last merging conflict)
2020-05-11 Implement ADS1015; bugfix in io.devices.pins; new prototype .ini file; implemented stubs in Hal
2020-05-12 updates to controller: (1) control pressured, and not dp/dt - dp/dt is too noisy (2) added get_target_waveform() function that returns a stepwise linear target function (3) updates to the balloon for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
2020-05-12 Feature implementation: ControlValve Response; Fleshing out of docstrings in vent.io; New ventilator configuration reflected in devices.ini (old moved to devices-old.ini); Additional sensors & valves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
2020-05-14 Added Sensor PCB documentation, version 1
2020-05-15 Implement a whole bunch of mock pigpio stuff, mostly to simulate a raw GPIO interface. Wrote some tests for io.devices.pins, and some tests for io.devices.valves [not done with those].
2020-05-15 bugfix in io.devices.valves and cleanup old test files
2020-05-17 PEEP valve readme
2020-05-17 Uploading CERN OHL license text and CAD files
    [3D_PRINTABLE_PEEP_VALVE.SLDASM, 3D_PRINTABLE_PEEP_VALVE.STEP, DIAPHRAGM_RETAINER_RING.STEP, DIAPHRAGM_RETAINER_RING.STL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]
2020-05-18 Continued work on mock-pigpio i2c tests & framework
2020-05-18 Tests for vent.io module (& maybe some fixes for bugs that were found during testing) ALso, revamped the Sensor data backend to use collections.deque, and rewrote the update/get interface to make sli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
2020-05-18 Draft D-Lite flow sensor implementation
2020-05-22 sending volume and flow from controller, reorganizing values, adding display attriute
2020-05-22 controls display current values.
2020-05-27 longer run on the pi, protocol pressure
2020-05-31 good round 3cm H2O
2020-06-02 plot pressure
2020-06-02 update to offset voltage
2020-06-02 more flow
2020-06-02 close valve in
2020-06-03 offset voltage
2020-06-03 time limit for stuck sensors
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2020-07-13 fixes to make the thing work
    flor inverted and /60
    correct sensor reads
2020-08-01 Adding breath detection mode button & removing peept control * made set_breath_detection methods for control module, coordinator, rpc * check for self.breath_detection in controller before doing voli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
2020-08-10 fix travis II
    maybe the sensors-check is stuck?
2020-08-10 fix travis III
    sensorvalues in the UI test seem to be the problem
2020-08-10 fix travis issue IV
    sensor and control seem to cause trouble
2020-08-11 Uploaded data files and Python scripts
    [valve_response_dlite_setup.csv]
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2020-08-12 fixing COPY_SET_PIP issue on HAPA
    - moving hapa warning to same check as creating the alarm so not multiply warned
    - reinstated dt=self._loop_update_time because i'm afraid of touching anything in the controller, but it seems like if _LOOP_UPDATE_TIME was 0, which is the default, that might cause problems
    - updated the erratic_dt test so use a simulated dt instead of actually waiting (since it's a simulation we can pretend however much time we want has elapsed)
    - updated erratic_dt test to wait on a specific number of breath cycles rather than a fixed time.
    - updated package_data in setup.py to ensure calibration data and CAD files are copied to distribution packages
2020-08-12 added pcb kicad files
    [actuators-rev2.kicad_pcb, actuators-rev2.sch, pressure-rev2.kicad_pcb, pressure-rev2.sch]
2020-08-13 little touchups for screenshot
    fix misnamed valve reset function in main
2020-08-14 refactoring into assets directory
    [3D_PRINTABLE_PEEP_VALVE.SLDASM, 3D_PRINTABLE_PEEP_VALVE.STEP, DIAPHRAGM_RETAINER_RING.STEP, DIAPHRAGM_RETAINER_RING.STL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]
2020-08-18 Uploading STL files 8/18/20
    [22MM_OD_TO_0.75_NPTM_ADAPTER.STL, EXPIRATORY_DAR_FILTER_BRACKET.STL, EXPIRATORY_OUTLET_BRACKET_TO_PEEP_DVC.STL, INLET_AIR_MAINFOLD_BRACKET_REV_2.STL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]
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2020-08-19 generated gerber files
    [actuators-rev2-B_Cu.gbl, actuators-rev2-B_Mask.gbs, actuators-rev2-B_SilkS.gbo, actuators-rev2-Edge_Cuts.gm1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]
2020-08-19 revised, added schematic images
    [actuators-rev2.sch, pressure-rev2-B_Cu.gbl, pressure-rev2-B_Mask.gbs, pressure-rev2-B_SilkS.gbo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]
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2020-08-19 added sensor pcb bom
    [sensor_pcb_bom.csv]
2020-08-19 updated sensor pcb bom
    [sensor_pcb_bom.csv]
2020-08-19 list edits
    [actuator_pcb_bom.csv]
2020-08-19 update bom csvs
    [actuator_pcb_bom.csv, sensor_pcb_bom.csv]
2020-08-19 update sensor bom
    [sensor_pcb_bom.csv]
2020-08-19 more bom updates
    [actuator_pcb_bom.csv, sensor_pcb_bom.csv]
2020-08-20 add powerio_bom
    [powerio_bom.csv]
2020-08-20 edit powerio bom
    [powerio_bom.csv]
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2020-08-24 fix cap error in bom
    [actuator_pcb_bom.csv, sensor_pcb_bom.csv]
2020-08-24 update schematic img and file for sensor board
    [pressure-rev2.sch]
2020-08-24 adding performance info
    [eua_test.csv]
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2020-08-26 few text updates
    [actuator_pcb_bom.csv, powerio_bom.csv, sensor_pcb_bom.csv]
2020-09-04 updated sensor pcb to swap pressure/flow sensor
    [sensor_pcb_bom.csv]
2020-09-04 updated sensor pcb schematic to reflect pressure/airflow sensor swap
    [pressure-rev2.sch]
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2020-10-02 added project bom
    [10jul2020_bom.csv]
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2020-10-06 Delete LEFT_SCREEN_MODULE_MOUNT.STL
    Outdated mounting strategy
    [LEFT_SCREEN_MODULE_MOUNT.STL]
2020-10-06 Delete RIGHT_SCREEN_MODULE_MOUNT.STL
    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
    [RIGHT_SCREEN_MODULE_MOUNT.STL]
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2020-10-19 Cleanup of the timeout mess
    ...and no pytest required in the controll module anymore
    [2020-10-19-18-36-11_controller_log.0.control_commands.csv, 2020-10-19-18-36-11_controller_log.0.derived_quantities.csv, 2020-10-19-18-36-11_controller_log.0.wa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]
2020-10-19 cleanup; didn't mean to push the logs...
    [2020-10-19-18-36-11_controller_log.0.control_commands.csv, 2020-10-19-18-36-11_controller_log.0.derived_quantities.csv, 2020-10-19-18-36-11_controller_log.0.wa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]
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2022-01-17 Version 1
    [1023N150_MANIFOLD_0.375_NPT_IN_0.25NPT_OUT.SLDPRT, 1777K410_NONADJUSTABLE MINIATURE AIR REGULATOR.SLDPRT, 1777K410_NONADJUSTABLE_MINIATURE_AIR_REGULATOR.SLDPRT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]
2022-01-19 updated BOM / docs
    [10_27_2020_bom_short.csv]
2022-01-27 [skip travis] Splitting BOM table
    [10_27_2020_bom_airway.csv, 10_27_2020_bom_electronics.csv, 10_27_2020_bom_etc.csv, 10_27_2020_bom_io.csv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]
2022-01-27 Fourth column breaks setting explicit widths, but removing that for now
    [10_27_2020_bom_airway.csv]
2022-02-02 Added v1 of pcbs and revision history readme
    [actuators-rev1.kicad_pcb, actuators-rev1.sch, actuators-rev2-B_Cu.gbl, actuators-rev2-B_Mask.gbs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]
